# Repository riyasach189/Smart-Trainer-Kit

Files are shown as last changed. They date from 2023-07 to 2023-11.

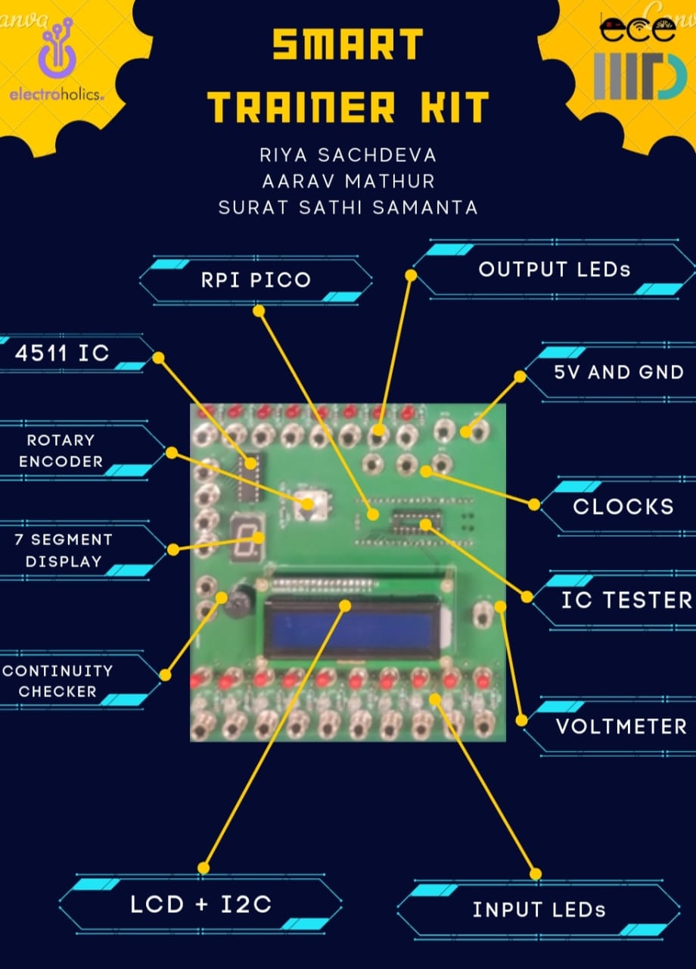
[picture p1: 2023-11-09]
Smart_Trainer_Kit_v2/Smart Trainer Kit.jpg

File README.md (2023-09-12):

## Background and Motivation:
- The Digital Trainer Kit serves as a vital tool for facilitating learning, teaching, and testing of digital electronic circuits.
- It plays a crucial role in the laboratory component of the Digital Circuits course offered in Semester 1 at IIIT-D.
- However, the current trainer kits deployed in the ECE labs suffer from drawbacks such as being bulky, expensive, and featuring redundant functions.

## Objectives:
- To find alternatives that are compact, lightweight, and reasonably priced, without compromising essential functionalities.
- To enhance the versatility and functionality of the proposed alternative, a microcontroller will be incorporated into the design. This addition will provide opportunities for future expansion and the inclusion of advanced features, empowering students to explore more complex digital circuits.

## Version 1
**BoM:**
```markdown
| Component                                     | Quantity | Price | Total Cost |
|-----------------------------------------------|----------|-------|------------|
| Arduino Board                                 | 1        | 550   | 550        |
| LEDs                                          | 22       | 0.8   | 17.6       |
| Resistors (330 Ohm)                           | 25       | 0.4   | 10         |
| Push Button Square Switch Self-Locking DPDT   | 10       | 5     | 50         |
| 4511 IC                                       | 1        | 21    | 21         |
| 7 Segment Display (Common Cathode)            | 1        | 7     | 7          |
| Passive Buzzer                                | 1        | 10    | 10         |
| 741 IC                                        | 1        | 9     | 9          |
| 4 mm Banana Sockets                           | 30       | 14.5  | 435        |
|                                               |          |       | 1109.6     |
```

**Features and Description:**
- A 12 V adapter powers the circuit. The Arduino has an inbuilt 12 V to 5 V converter. For the rest of the circuit, a Buck-Boost Converter is used.
- Nested 'for loops' are programmed in the Arduino to provide continuous clock signals of 3 frequencies - 0.1 Hz, 1 Hz, 10 Hz.
- The Continuity Checker can be used to debug faulty connections in a circuit.
- The Voltage Detector returns a HIGH value (LED turns on) when the voltage at a given point exceeds 2.5 V (to accommodate both the CMOS and TTL logic levels) in reference to the circuit ground, and returns a LOW value otherwise. A voltage divider is used between 5 V and GND to set the benchmark voltage at 2.5 V.
- The 4511 IC is connected to a 7-segment display to convert binary input to decimal digits (0 to 9).
- The Input LEDs can be operated using the Push Button switches connected to them.
- There are designated signal detector pins on the Arduino, which can be used to plot the clock signals on the Serial Plotter.

**Problems Encountered:**
- TinkerCad is not a reliable tool for large circuits; not recommended. They have also removed many components from their library.
- Initially, we planned to keep the clock frequencies variable, but Arduino can only run one infinite loop at a time. So, we decided to use nested 'for loops' to provide clock signals.
- We were trying to use a Common Cathode 7 segment display with a 7447 IC before we realized that that IC drives Common Anode displays.
- We found the 7805 IC unstable for voltage conversion, so we switched to a Buck-Boost Converter.
- When we kept the circuit on for a long time, the Input LEDs started flickering when switched ON. This issue remains unresolved. Possible reasons are:
  - The 12 V adapter could not meet the power requirements.
  - Arduino could not meet the power requirements.
  - The plastic and metal holes in the breadboard did not align, leading to loose connections.
  - Poor soldering on Buck-Boost Converter.
- We planned to use toggle switches in the circuit, but they were panel mount instead of PCB mount. So we switched to push button switches.

**Resources:**
- KiCad - PCB Design
- [7 Segment Display with 4511 IC](https://youtu.be/KZTwr95eINc)
- [Arduino for Beginners](https://youtu.be/d8_xXNcGYgo)
- [How to Use DPDT Switches](https://youtu.be/f0EMblUCp54)

## Version 2
**BoM:**
```markdown
| Component                                | Quantity | Price | Total Cost |
|------------------------------------------|----------|-------|------------|
| RPi Pico Board                           | 1        | 345   | 345        |
| LEDs                                     | 18       | 0.8   | 14.4       |
| Resistors (330 Ohm)                      | 24       | 0.4   | 9.6        |
| Toggle switches                          | 10       | 20    | 200        |
| 4511 IC                                  | 1        | 21    | 21         |
| 7 Segment Display (Common Cathode)       | 1        | 7     | 7          |
| DIP Socket (16 Pin)                      | 1        | 3     | 3          |
| ZIF Socket (16 Pin)                      | 1        | 50    | 50         |
| Passive Buzzer                           | 1        | 10    | 10         |
| 2 mm Banana Sockets                      | 30       | 26    | 780        |
| Rotary Encoder                           | 1        | 50    | 50         |
| LCD (16 x 2) + I2C                       | 1        | 188   | 188        |
| 18 mm Standoffs                          | 4        | 16    | 64         |
| Potentiometer                            | 1        | 6     | 6          |
| Female Headers                           | 44       | 1.125 | 49.5       |
|                                          |          |       | 1797.5     |
```

**Features and Description:**
- A 5 V power supply powers the circuit.
- State machines on the rp2040 to provide continuous clock signals of 3 frequencies - 1 Hz, 5 Hz, 10 Hz.
- The Continuity Checker can be used to debug a circuit.
- The 4511 IC is connected to a 7-segment display to convert binary input to decimal digits (0 to 9).
- The Input LEDs can be operated using the toggle switches connected to them.
- The rotary menu is displayed on the LCD screen and operated using the rotary encoder. It has 2 options: IC Tester and Voltmeter.
- If 'Voltmeter' is selected, the LCD displays the voltage (in reference to the circuit GND) at the given point. To exit the voltmeter mode, click on the rotary encoder button.
- To use the IC Tester, plug the IC into the DIP socket (If it's a 14 Pin IC, leave the last 2 pins of the DIP Socket empty, i.e., start from the beginning of the DIP Socket). Then, select which IC you wish to test. The LCD will display '[ ]' for every gate that is functioning and '[!]' for every gate that is not functioning in the IC (keeping the IC notch on the left).

**Problems Encountered:**
- RPi Pico should connect to a Windows system in theory, but we were only able to establish connection in Linux systems.
- To connect an RPi Pico, we require a microUSB to USB cable which supports data and charge transfer, not just charge transfer.
- Pico's LED light did not turn ON the moment it was connected to the power supply, which led us to believe that the Pico was faulty (which is not true).
- It took us some time to decide between using a raw rotary encoder or one mounted on a PCB, due to differences in available online resources. We settled on a PCB-mounted encoder but re-soldered its header pins to be more breadboard-friendly.
- We decided to use an I2C to connect the LCD screen to reduce the number of pins required on RPi Pico. This left extra pins for IC Tester and future expansion.
- RPi Pico is a dual-core processor in theory, but we were unable to use its multithreading functionality. We spent a long time trying to generate clock signals from Pico on the second thread, but Pico could only process one thread at a time. We finally decided to use 555 timers to generate clock signals.
- For the voltmeter, we wanted a range of (0, 5) V but the analog read pins of RPi Pico can take a maximum input of 3.3 V. So we used a voltage divider to map the range (0, 5) V onto (0, 3.3) V, then mapped that back to (0, 5) V in the code.
- We were later able to implement a clock without the use of separate threads through state machines on three different pins; however, having a variable clock was still not possible, and we settled on having three constant clock signals.
- We replaced push button switches with toggle switches because they were shorting the GND and VCC plane in the ON configuration. We believe push button switches are available in 2 different pinouts, but they look the same on the outside, ie. it is not possible to tell from the outside which type of push button switch it is. Also, toggle switches offer more tactile feedback and are a better choice.
- The biggest bottleneck in the whole design process was finding a PCB manufacturer.
- We realised we had missed some traces in the PCB when we assembled the first prototype, so we added them later.
- We had missed the Vcc and GND connection of the 4511 IC, and for some reason, it was causing the IC to heat up whenever we turned the RPi Pico on. This problem was resolved when we provided Vcc and GND to the IC.

**Resources:**
- [Rotary Encoder with RPi Pico](https://youtu.be/sgnEUxeNxpM)
- [RPi Pico for Beginners](https://youtu.be/1WDagiA8fdU)
- [Connect LCD to RPi Pico using I2C](https://www.tomshardware.com/how-to/lcd-display-raspberry-pi-pico)
- [555 Timer IC in Astable Mode](https://youtu.be/iJYm_BGqa1A)
- [555 Timer Frequency Calculator in Astable Mode](https://ohmslawcalculator.com/555-astable-calculator)
- [State Machines on RPi Pico](https://www.ourpcb.com/programmable-io.html)
  
## Contributors:
- Dr. Rahul Gupta - Manager, Research Labs (Supervisor of the Project)
- [Riya Sachdeva - EVE, BTech 2026](https://github.com/riyasach189)
- [Surat Sathi Samanta - EVE, BTech 2026](https://github.com/kio42069/)
- [Aarav Mathur - CSSS, BTech 2026](https://github.com/13100d/)

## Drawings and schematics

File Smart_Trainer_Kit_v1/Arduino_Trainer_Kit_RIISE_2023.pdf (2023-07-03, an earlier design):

# ARDUINO

# INTEGRATED

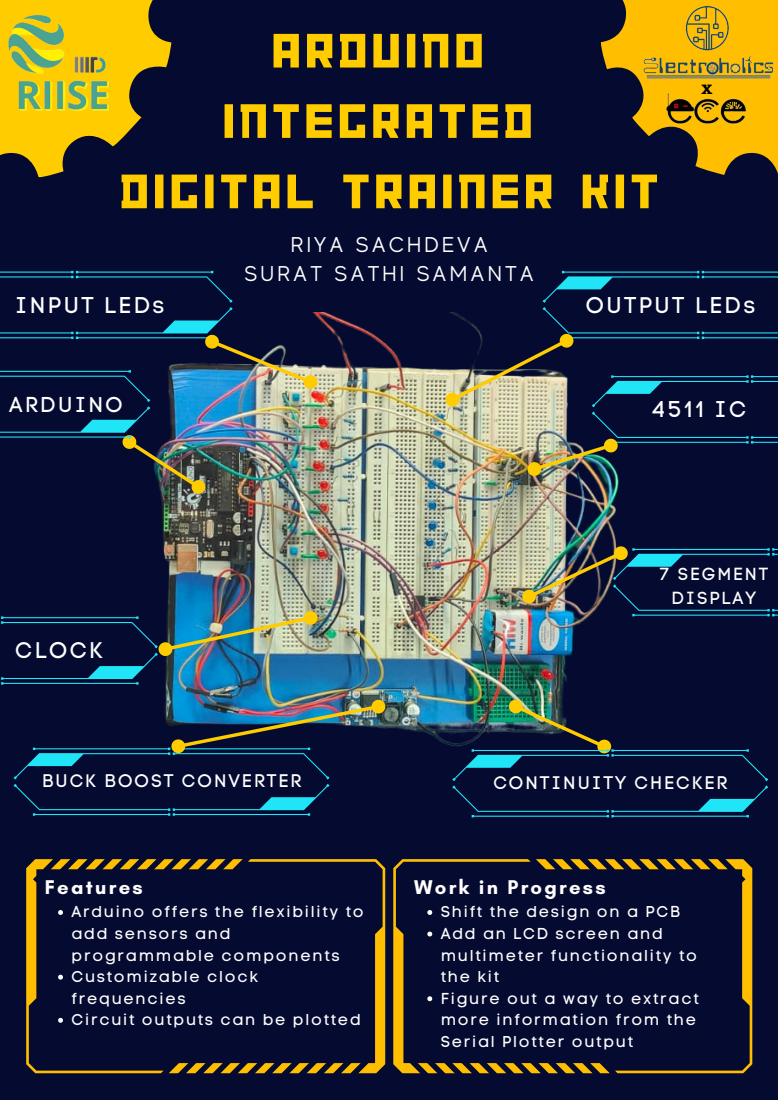
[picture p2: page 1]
ARDUINO; CONTINUITY CHECKER; INPUT LEDs; OUTPUT LEDs; 7 SEGMENT DISPLAY; CLOCK

DIGITAL TRAINER KIT

R I YA SA C HDE VA
SURAT SATHI SA M ANTA

BUCK BOOST CONVERTER

Features
Arduino offers the flexibility to
add sensors and
programmable components
Customizable clock
f requencies
Ci rcuit outputs can be plotted

Work in Progress
Shift the design on a PCB
Add an LCD screen and
multimeter functionality to
the kit
Figure out a way to ext ract
more information f rom the
Ser ial Plotter output

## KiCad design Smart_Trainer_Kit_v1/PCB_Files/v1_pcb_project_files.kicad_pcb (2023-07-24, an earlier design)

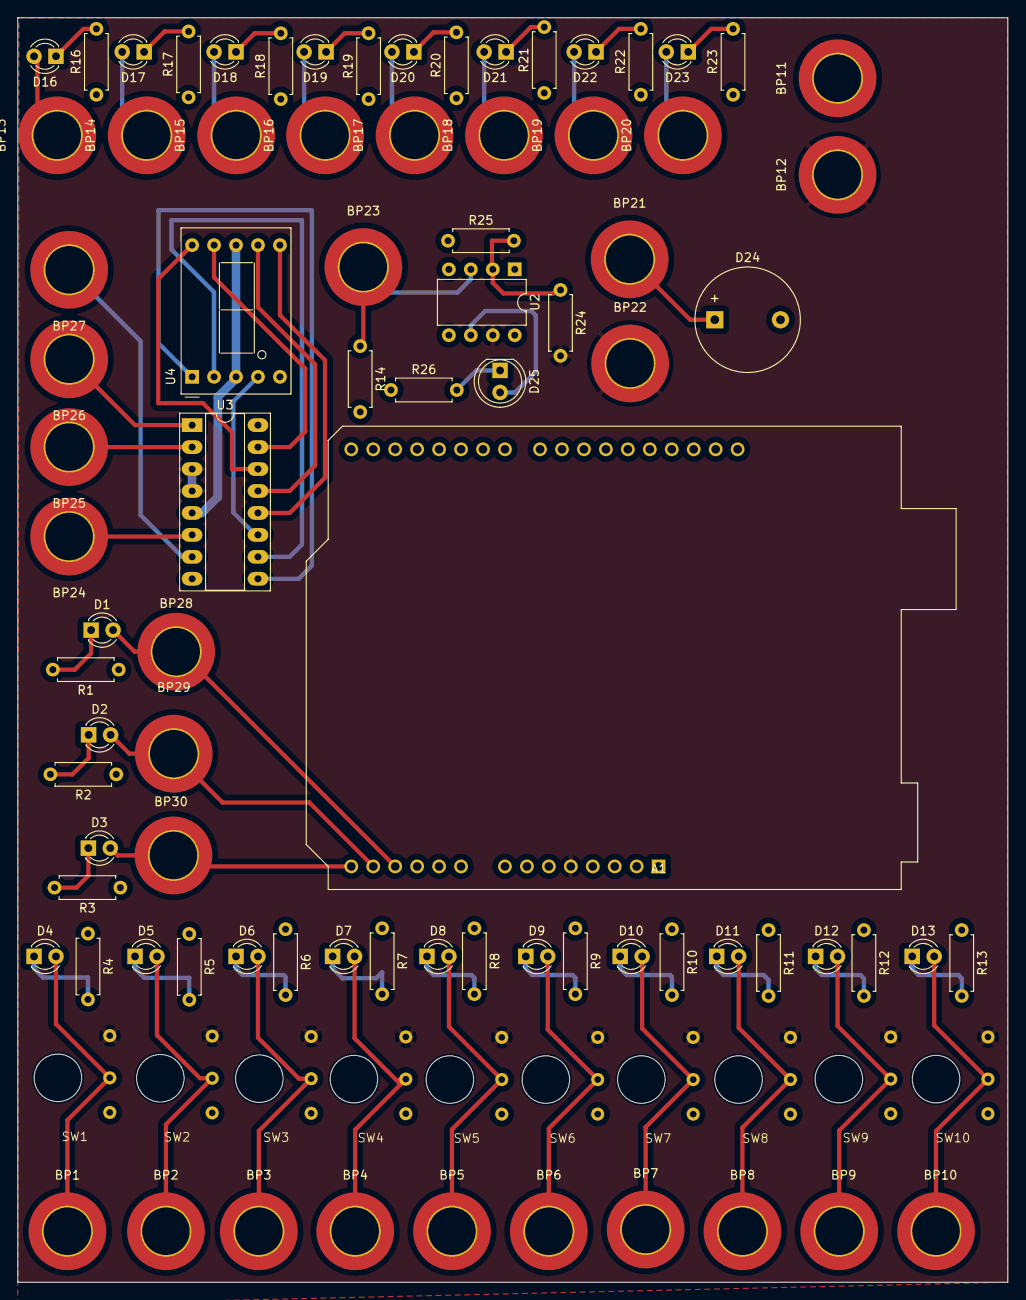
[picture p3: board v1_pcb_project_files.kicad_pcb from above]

Board: 2 copper layers, 114.5 x 146.3 mm, 92 parts (0 on the bottom side), 60 nets.

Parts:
A1: Arduino_UNO_R3
BP1, BP2, BP3, BP4, BP5, BP6, BP7, BP8, BP9, BP10, BP11, BP12, BP13, BP14, BP15, BP16, BP17, BP18, BP19, BP20, BP21, BP22, BP23, BP24, BP25, BP26, BP27, BP28, BP29, BP30: banana plug; banana_plug(modified thickness)
D1, D2, D3, D4, D5, D6, D7, D8, D9, D10, D11, D12, D13, D16, D17, D18, D19, D20, D21, D22, D23: CQY99; LED_D3.0mm
D24: LED; Buzzer_12x9.5RM7.6
D25: LED; LED_D5.0mm_IRGrey
R1, R2, R3, R4, R5, R6, R7, R8, R9, R10, R11, R12, R13, R14, R16, R17, R18, R19, R20, R21, R22, R23, R24, R25, R26: 330; R_Axial_DIN0207_L6.3mm_D2.5mm_P7.62mm_Horizontal
SW1, SW2, SW3, SW4, SW5, SW6, SW7, SW8, SW9, SW10: SW_Push_SPDT; SPDT_platemount_switch(platemount)
U2: LM741; DIP-8_W7.62mm
U3: CD4511B; DIP-16_W7.62mm_Socket_LongPads
U4: D168K; D1X8K

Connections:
+5V: A1.5 (+5V), BP12.1 (A), BP22.1 (A), R24.2, SW1.1 (A), SW2.1 (A), SW3.1 (A), SW4.1 (A), SW5.1 (A), SW6.1 (A), SW7.1 (A), SW8.1 (A), SW9.1 (A), SW10.1 (A), U2.7 (V+), U3.3 (~LT), U3.4 (~BI)
/V(input): BP23.1 (A), R14.1, U2.3 (+)
GNDREF: A1.29 (GND), BP11.1 (A), D24.2 (A), R1.1, R2.1, R3.1, R4.1, R5.1, R6.1, R7.1, R8.1, R9.1, R10.1, R11.1, R12.1, R13.1, R14.2, R16.1, R17.1, R18.1, R19.1, R20.1, R21.1, R22.1, R23.1, R25.1, R26.1, SW1.3 (C), SW2.3 (C), SW3.3 (C), SW4.3 (C), SW5.3 (C), SW6.3 (C), SW7.3 (C), SW8.3 (C), SW9.3 (C), SW10.3 (C), U2.4 (V-), U3.5 (~EL), U4.3 (CC), U4.8 (CC)
unnamed: A1.12 (A3), BP28.1 (A), D1.2 (A)
unnamed: BP1.1 (A), D4.2 (A), SW1.2 (B)
unnamed: BP2.1 (A), D5.2 (A), SW2.2 (B)
unnamed: BP3.1 (A), D6.2 (A), SW3.2 (B)
unnamed: BP4.1 (A), D7.2 (A), SW4.2 (B)
unnamed: BP5.1 (A), D8.2 (A), SW5.2 (B)
unnamed: BP6.1 (A), D9.2 (A), SW6.2 (B)
unnamed: BP7.1 (A), D10.2 (A), SW7.2 (B)
unnamed: BP8.1 (A), D11.2 (A), SW8.2 (B)
unnamed: BP9.1 (A), D12.2 (A), SW9.2 (B)
unnamed: BP10.1 (A), D13.2 (A), SW10.2 (B)
unnamed: BP13.1 (A), D16.2 (A)
unnamed: BP14.1 (A), D17.2 (A)
unnamed: BP15.1 (A), D18.2 (A)
unnamed: BP16.1 (A), D19.2 (A)
unnamed: BP17.1 (A), D20.2 (A)
unnamed: BP18.1 (A), D21.2 (A)
unnamed: BP19.1 (A), D22.2 (A)
unnamed: BP20.1 (A), D23.2 (A)
unnamed: BP21.1 (A), D24.1 (K)
unnamed: BP24.1 (A), U3.6 (DD)
unnamed: BP25.1 (A), U3.2 (DC)
unnamed: BP26.1 (A), U3.1 (DB)
unnamed: BP27.1 (A), U3.7 (DA)
unnamed: A1.13 (SDA/A4), BP29.1 (A), D2.2 (A)
unnamed: A1.14 (SCL/A5), BP30.1 (A), D3.2 (A)
unnamed: D1.1 (K), R1.2
unnamed: D2.1 (K), R2.2
unnamed: D3.1 (K), R3.2
unnamed: D4.1 (K), R4.2
unnamed: D5.1 (K), R5.2
unnamed: D6.1 (K), R6.2
unnamed: D7.1 (K), R7.2
unnamed: D8.1 (K), R8.2
unnamed: D9.1 (K), R9.2
unnamed: D10.1 (K), R10.2
unnamed: D11.1 (K), R11.2
unnamed: D12.1 (K), R12.2
unnamed: D13.1 (K), R13.2
unnamed: D16.1 (K), R16.2
unnamed: D17.1 (K), R17.2
unnamed: D18.1 (K), R18.2
unnamed: D19.1 (K), R19.2
unnamed: D20.1 (K), R20.2
unnamed: D21.1 (K), R21.2
unnamed: D22.1 (K), R22.2
unnamed: D23.1 (K), R23.2
unnamed: D25.2 (A), U2.6
unnamed: D25.1 (K), R26.2
unnamed: R24.1, R25.2, U2.2 (-)
unnamed: U3.13 (Qa), U4.7 (A)
unnamed: U3.12 (Qb), U4.6 (B)
unnamed: U3.11 (Qc), U4.4 (C)
unnamed: U3.10 (Qd), U4.2 (D)
unnamed: U3.9 (Qe), U4.1 (E)
unnamed: U3.15 (Qf), U4.9 (F)
unnamed: U3.14 (Qg), U4.10 (G)

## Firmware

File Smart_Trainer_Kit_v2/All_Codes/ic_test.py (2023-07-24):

#CD4071

from machine import *
from utime import *

p1 = Pin(16,Pin.OUT)
p2 = Pin(17,Pin.OUT)
p3 = Pin(18,Pin.IN)
p4 = Pin(19,Pin.IN)
p5 = Pin(20,Pin.OUT) 
p6 = Pin(21,Pin.OUT)
p7 = Pin(22,Pin.OUT)
#p8_GND 
p9 = Pin(2, Pin.OUT)
p10 = Pin(3, Pin.OUT)
p11 = Pin(4,Pin.OUT)
p12 = Pin(5,Pin.IN)
p13 = Pin(6,Pin.IN)
p14 = Pin(7,Pin.OUT)
p15 = Pin(8,Pin.OUT)
#p16_Vcc

p7.off()
p9.off()


lst = [
    [0,0,0],
    [0,1,1],
    [1,0,1],
    [1,1,1]
    ]

print("Gate 1: ")
for i in lst:
    p1.value(i[0])
    p2.value(i[1])
    sleep(0.05)
    print(p3.value() == i[2])

print("Gate 2: ")
for i in lst:
    p5.value(i[0])
    p6.value(i[1])
    sleep(0.05)
    print(p4.value() == i[2])

print("Gate 3: ")
for i in lst:
    p10.value(i[0])
    p11.value(i[1])
    sleep(0.05)
    print(p12.value() == i[2])

print("Gate 4: ")
for i in lst:
    p14.value(i[0])
    p15.value(i[1])
    sleep(0.05)
    print(p13.value() == i[2])

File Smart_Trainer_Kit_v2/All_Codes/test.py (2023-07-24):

#from gate_tester import *
#print(gatetester("CD4001"))

from machine import Pin
from time import sleep

p1 = Pin(2,Pin.OUT)
p2 = Pin(3,Pin.OUT)
p3 = Pin(4,Pin.IN)
g = Pin(8,Pin.OUT)
g.value(0)

lst = [
    [0,0,1],
    [0,1,0],
    [1,0,0],
    [1,1,0]
    ]


for i in lst:
    newlst = ""
    p1.value(i[0])
    p2.value(i[1])
    sleep(0.05)
    if p3.value() == i[2]:
        print(True)
    else:
        print(False)

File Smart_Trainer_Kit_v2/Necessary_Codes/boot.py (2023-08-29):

from pio_clock import *
from machine import *
import utime
from rotary_encoder_classes import *
from constants import *
from pico_i2c_lcd import I2cLcd
from gate_tester import *
i2c = machine.I2C(0, sda=machine.Pin(0), scl=machine.Pin(1), freq=400000)

#status led
led = Pin(25, Pin.OUT)
led.value(1)

#clocks
sm_1.active(1)
sm_5.active(1)
sm_10.active(1)

#gate tester
ic_tester_screen = 0
ic_selected = ""

#voltmeter
pot_val = machine.ADC(0)
conversion_factor = 5/65535

#lcd
I2C_ADDR = i2c.scan()[0]
lcd = I2cLcd(i2c, I2C_ADDR, 2, 16)

#rotary encoder
last_Enc_Counter_1 = 0
Enc_Counter_1 = 0
Last_Qtr_Cntr_1 = 0
Qtr_Cntr_1 = 0
error_1 = 0

Enc_1 = R_Encoder(15, 14)
Enc_1.DisplayPins()
Enc_1.Reset_Counter()

Enc_1_SW = machine.Pin(13, machine.Pin.IN, machine.Pin.PULL_UP)
Enc_1_SW_State = "UP"

#main menu
pointer = 0
ic_menu_pointer = -1
main_menu_options = ["> IC Tester", "> Voltmeter"]
ic_options = len(ic_tester_options)
lcd = I2cLcd(i2c, I2C_ADDR, 2, 16)
lcd.putstr(main_menu_options[pointer])

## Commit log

2023-07-07 Create voltmeter
2023-07-24 cleaned uo
    [Copy of Trainer Kit Prototype.kicad_pcb, Copy of Trainer Kit Prototype.kicad_sch, trainer kit arduino proto.kicad_pcb, v1_pcb_project_files.kicad_pcb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]
2023-08-29 Update boot.py
    quality of life improvement fucking power led
2023-12-29 pcb files
    [Copy of Trainer Kit Prototype-B_Cu.gbr, Copy of Trainer Kit Prototype-B_Mask.gbr, Copy of Trainer Kit Prototype-B_Paste.gbr, Copy of Trainer Kit Prototype-B_Si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]
2024-01-02 Update constants.py
    shuffle gpio allocation ( make path routing for pcb easier )
